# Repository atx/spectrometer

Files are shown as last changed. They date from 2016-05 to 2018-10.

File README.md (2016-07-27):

# Alpha Spectrometer

Alpha spectrometer developed during my internship at the [IEAP](http://www.utef.cvut.cz/ieap).



Pu-239 Am-241 Cm-244 spectrum (on bare die BPW34 in vacuum)



## Protocol

### General structure

```
|----------|---------
|   type   | content...
|----------|---------
```

If the device receives a packet with invalid type, it responds with an ERROR
packet with EUNKNOWN error type.

### Host->Device

#### NOP

This does not do anything, it is recommended to send a bunch of NOPs on opening
the serial port to flush any data which might have been left in the device input
buffer.
```
|----------|
|   0x01   |
|----------|
```
#### PING

Used by host to check whether the device is alive. Device should respond with PONG.
```
|----------|
|   0x02   |
|----------|
```
#### GET

Used by host to get basic properties. Device should respond with GETRESP.
```
|----------|---------|
|   0x03   | propid  |
|----------|---------|
```
#### SET

Used by host to set basic properties. Propval length depends on the property being
set. Note that multi byte values should be sent in little endian.
```
|----------|---------|----------
|   0x04   | propid  | propval...
|----------|---------|----------
```
#### START

Start sampling and sending events.
```
|----------|
|   0x05   |
|----------|
```
#### END

End sampling and sending events.
```
|----------|
|   0x06   |
|----------|
```
### Device->Host

The most significant bit of the type field is always set to 1.

#### PONG

Sent as response to host PING.
```
|----------|
|   0x82   |
|----------|
```
#### EVENT

Send event (little endian).
```
|----------|----------|----------|
|   0x87   |   low    |   high   |
|----------|----------|----------|
```
#### GETRESP
```
|----------|----------|----------
|   0x83   |  propid  |  value...
|----------|----------|----------
```
The value length depends on the propid and the byte order is little endian.

#### WAVE

Sends event waveform. This is currently not yet implemented.
```
|----------|----------|----------
|   0x88   |  length  |  <length> samples, 2 bytes each, Big endian
|----------|----------|----------
```
#### ERROR
```
|----------|----------|
|   0xff   |  errno   |
|----------|----------|
```
Sent on errors.
errno:
  =  1  EUNKNOWN
    -- Sent on unknown packet type received
  =  2  EINKEY
    -- Sent on invalid key in GET/SET packet
  =  3  EINOP
    -- Sent on invalid operation on an existing key (unsuported read/write)

### Properties

#### PROP_FW (0x01)
length = 2

Firmware version version.

#### PROP_THRESH (0x02)
length = 2

Event trigger threshold.

#### PROP_BIAS (0x03)
length = 1

Set to 1 if the internal bias generator should be enabled.

#### PROP_AMP (0x04)
length = 1

Set to 1 if the internal x6 amplifier should be enabled.

#### PROP_RTHRESH (0x05)
length = 2

If the value is > 0, the events are further filtered based on whether their falling edge
is at least N samples longer than the rising edge.

#### PROP_SERNO (0x06)
length = 2

Serial number of the device. Set at compile time using `make SERNO=X`

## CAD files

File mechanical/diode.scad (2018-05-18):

difference() {
	minkowski() {
		cube([16, 16, 6], center=true);
		cylinder(r=2, h=0.01, $fn=100);
	}
	translate([0, 0, -0.5])
		cube([17, 15.5, 4], center=true);
	translate([0, 0, 2])
		cube([9, 3, 5], center=true);
}

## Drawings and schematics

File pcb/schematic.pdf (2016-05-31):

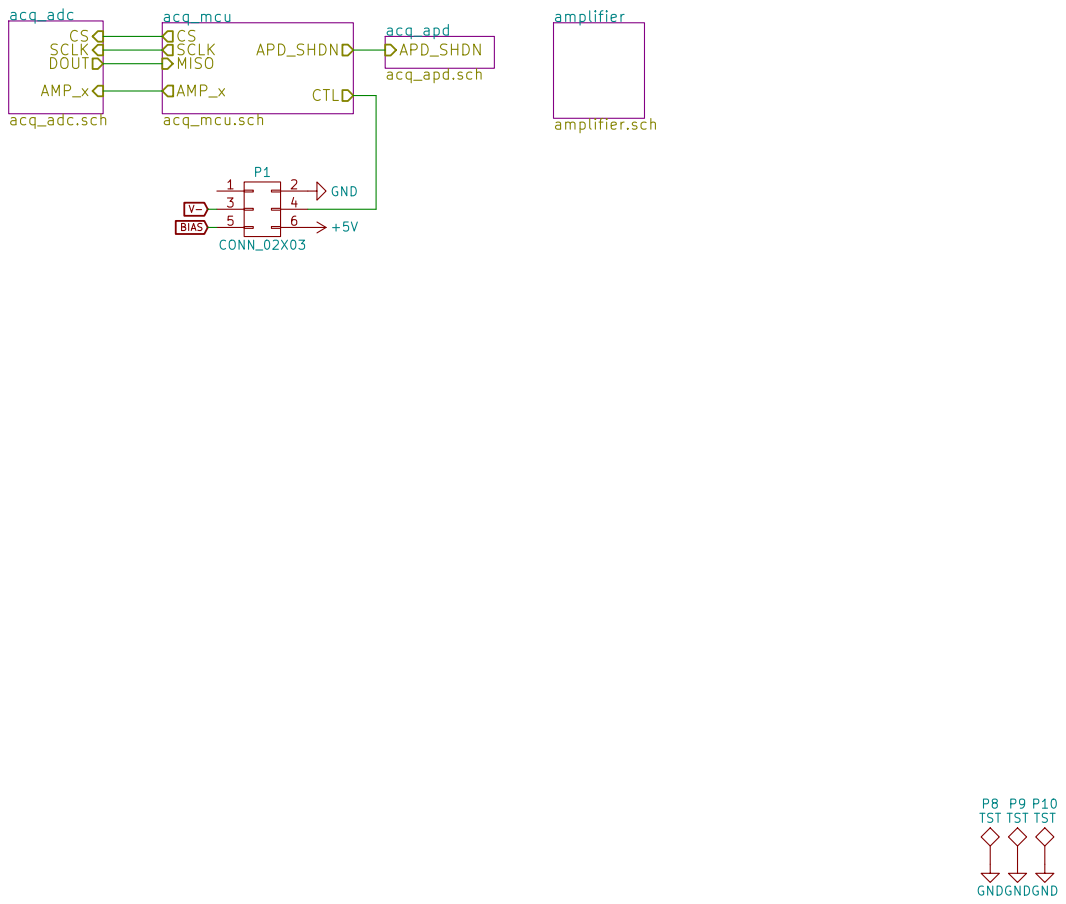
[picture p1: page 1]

Institute of Experimental and Applied Physics P8 TST GND

File: pcb.sch Sheet: /
Id: 1/5 Title: Root

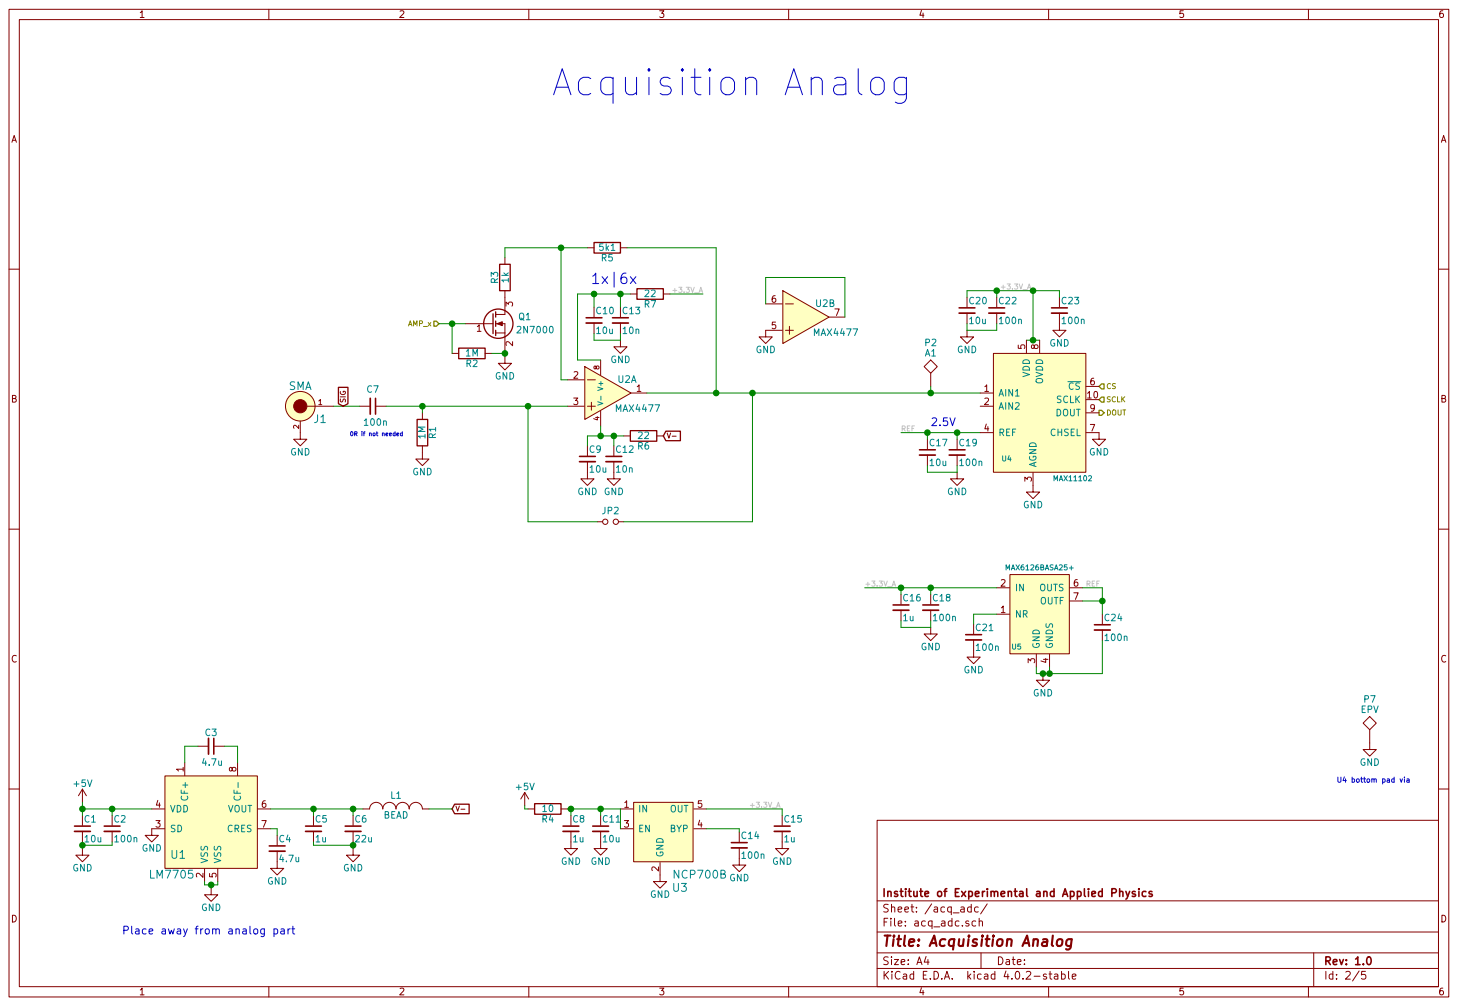
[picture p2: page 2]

U4 bottom pad via SIG

Institute of Experimental and Applied Physics
Sheet: /acq_adc/
File: acq_adc.sch
Id: 2/5 Title: Acquisition Analog

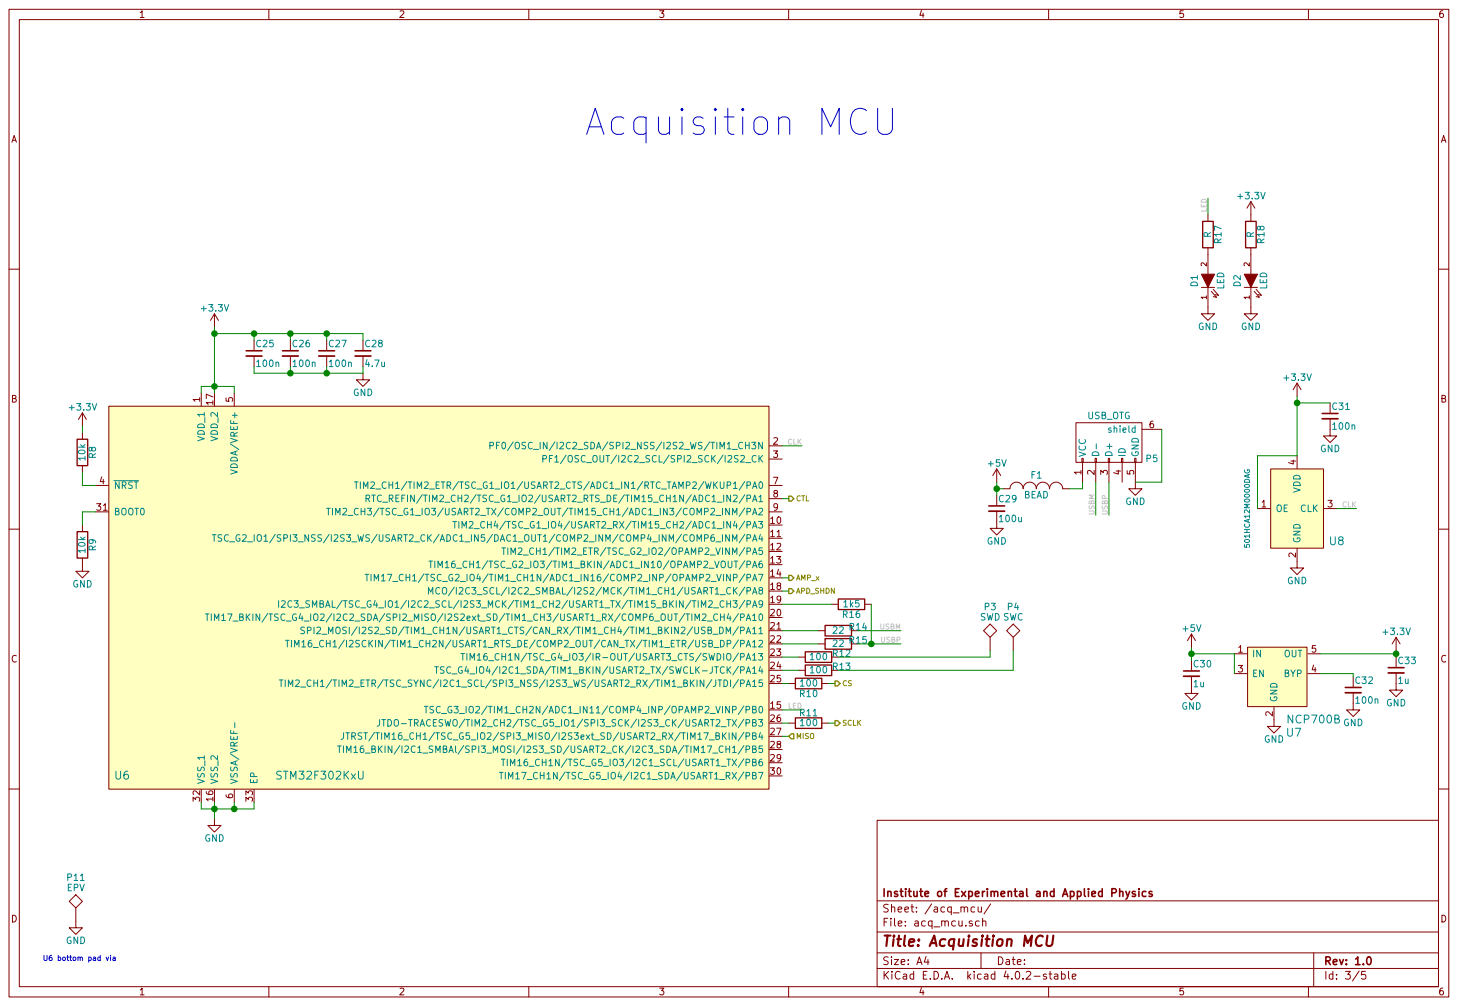
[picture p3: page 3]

5 VSSA/VREF- 6 TIM2_CH1/TIM2_ETR/TSC_G1_IO1/USART2_CTS/ADC1_IN1/RTC_TAMP2/WKUP1/PA0 7 RTC_REFIN/TIM2_CH2/TSC_G1_IO2/USART2_RTS_DE/TIM15_CH1N/ADC1_IN2/PA1 8 TIM2_CH3/TSC_G1_IO3/USART2_TX/COMP2_OUT/TIM15_CH1/ADC1_IN3/COMP2_INM/PA2 9 TIM2_CH4/TSC_G1_IO4/USART2_RX/TIM15_CH2/ADC1_IN4/PA3 10 TIM17_BKIN/TSC_G4_IO2/I2C2_SDA/SPI2_MISO/I2S2ext_SD/TIM1_CH3/USART1_RX/COMP6_OUT/TIM2_CH4/PA10 20 TIM17_CH1N/TSC_G5_IO4/I2C1_SDA/USART1_RX/PB7 30 TSC_G2_IO1/SPI3_NSS/I2S3_WS/USART2_CK/ADC1_IN5/DAC1_OUT1/COMP2_INM/COMP4_INM/COMP6_INM/PA4 11 SPI2_MOSI/I2S2_SD/TIM1_CH1N/USART1_CTS/CAN_RX/TIM1_CH4/TIM1_BKIN2/USB_DM/PA11 21 BOOT0 31 TIM2_CH1/TIM2_ETR/TSC_G2_IO2/OPAMP2_VINM/PA5 12 TIM16_CH1/I2SCKIN/TIM1_CH2N/USART1_RTS_DE/COMP2_OUT/CAN_TX/TIM1_ETR/USB_DP/PA12 22 VSS_1 32 TIM16_CH1/TSC_G2_IO3/TIM1_BKIN/ADC1_IN10/OPAMP2_VOUT/PA6 13 TIM16_CH1N/TSC_G4_IO3/IR-OUT/USART3_CTS/SWDIO/PA13 23 EP 33 TIM17_CH1/TSC_G2_IO4/TIM1_CH1N/ADC1_IN16/COMP2_INP/OPAMP2_VINP/PA7 14 TSC_G4_IO4/I2C1_SDA/TIM1_BKIN/USART2_TX/SWCLK-JTCK/PA14 24 TSC_G3_IO2/TIM1_CH2N/ADC1_IN11/COMP4_INP/OPAMP2_VINP/PB0 15 TIM2_CH1/TIM2_ETR/TSC_SYNC/I2C1_SCL/SPI3_NSS/I2S3_WS/USART2_RX/TIM1_BKIN/JTDI/PA15 25 VSS_2 16

Institute of Experimental and Applied Physics
Sheet: /acq_mcu/
File: acq_mcu.sch
Id: 3/5 Title: Acquisition MCU

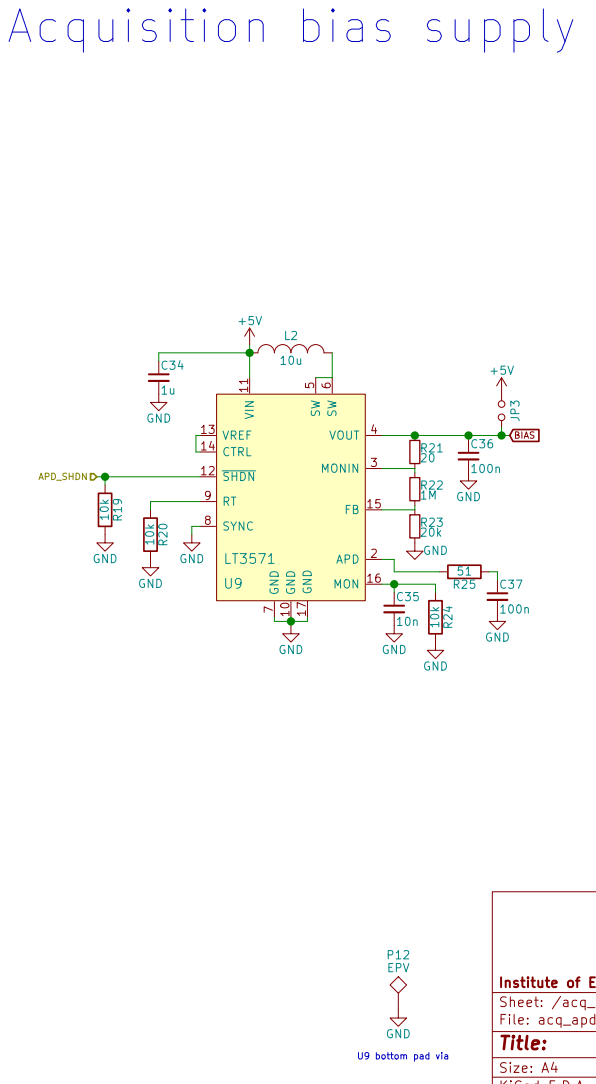
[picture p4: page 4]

7 SYNC 8 RT 9 GND 10 VIN 11 SHDN 12 VREF 13 CTRL 14 FB 15 MON 16 GND 17 U9

LT3571 GND GND 10k R20 GND 10k R19 GND

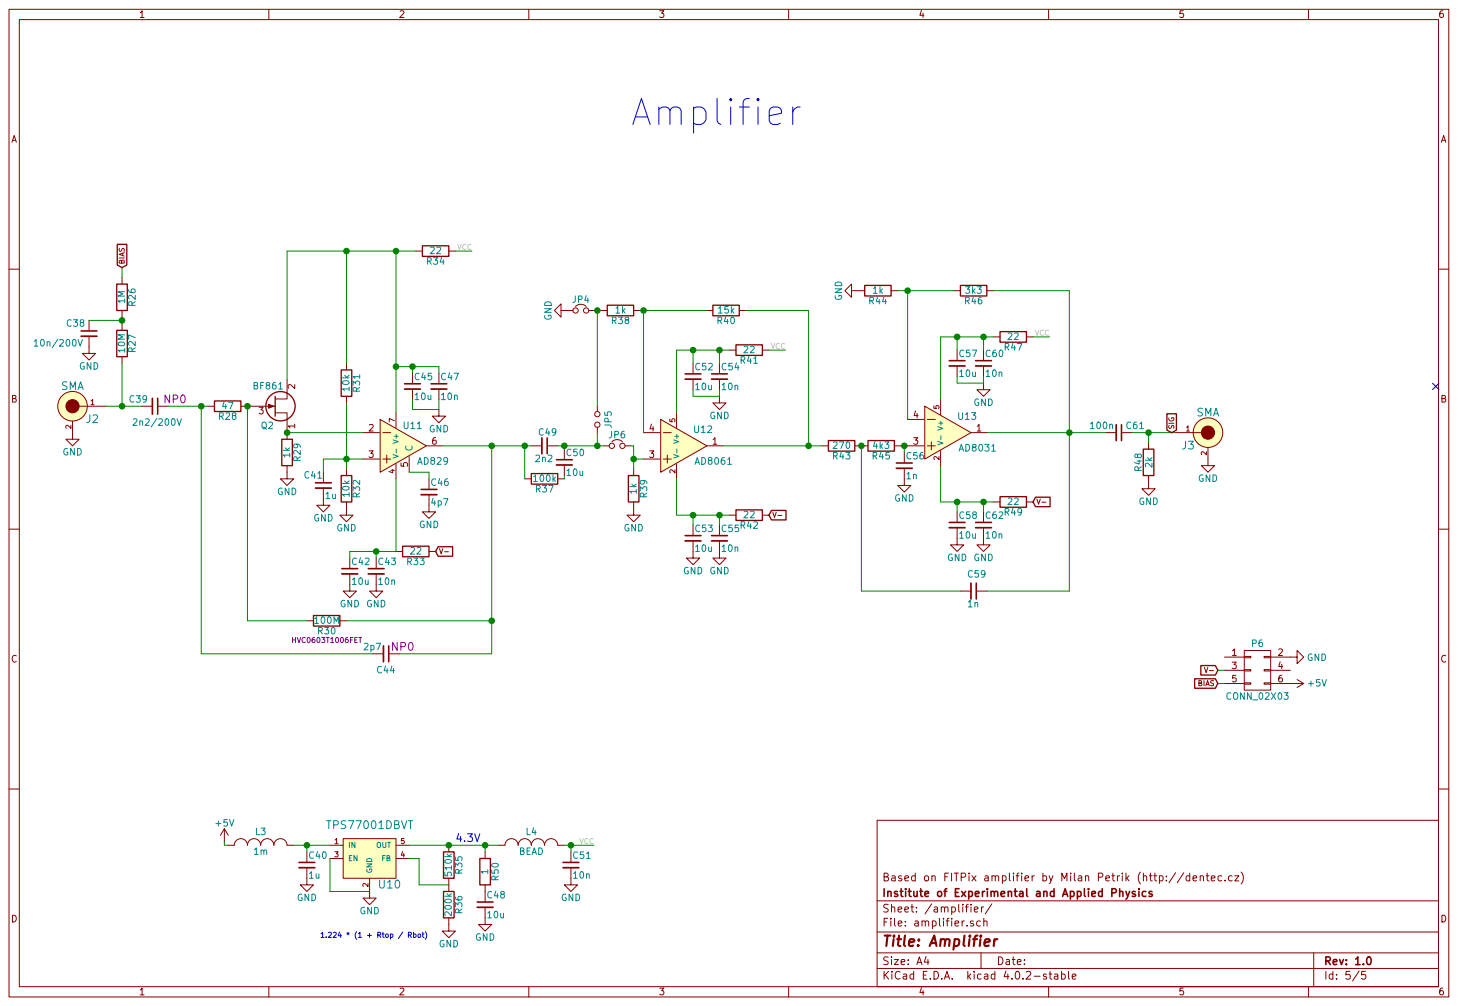
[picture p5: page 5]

2 EN 3 FB 4 OUT 5 U10 TPS77001DBVT GND

Based on FITPix amplifier by Milan Petrik (http://dentec.cz)
Institute of Experimental and Applied Physics
Sheet: /amplifier/
File: amplifier.sch
Id: 5/5 Title: Amplifier

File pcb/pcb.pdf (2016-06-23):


Institute of Experimental and Applied Physics P8 TST GND

File: pcb.sch Sheet: /
Id: 1/5 Title: Root

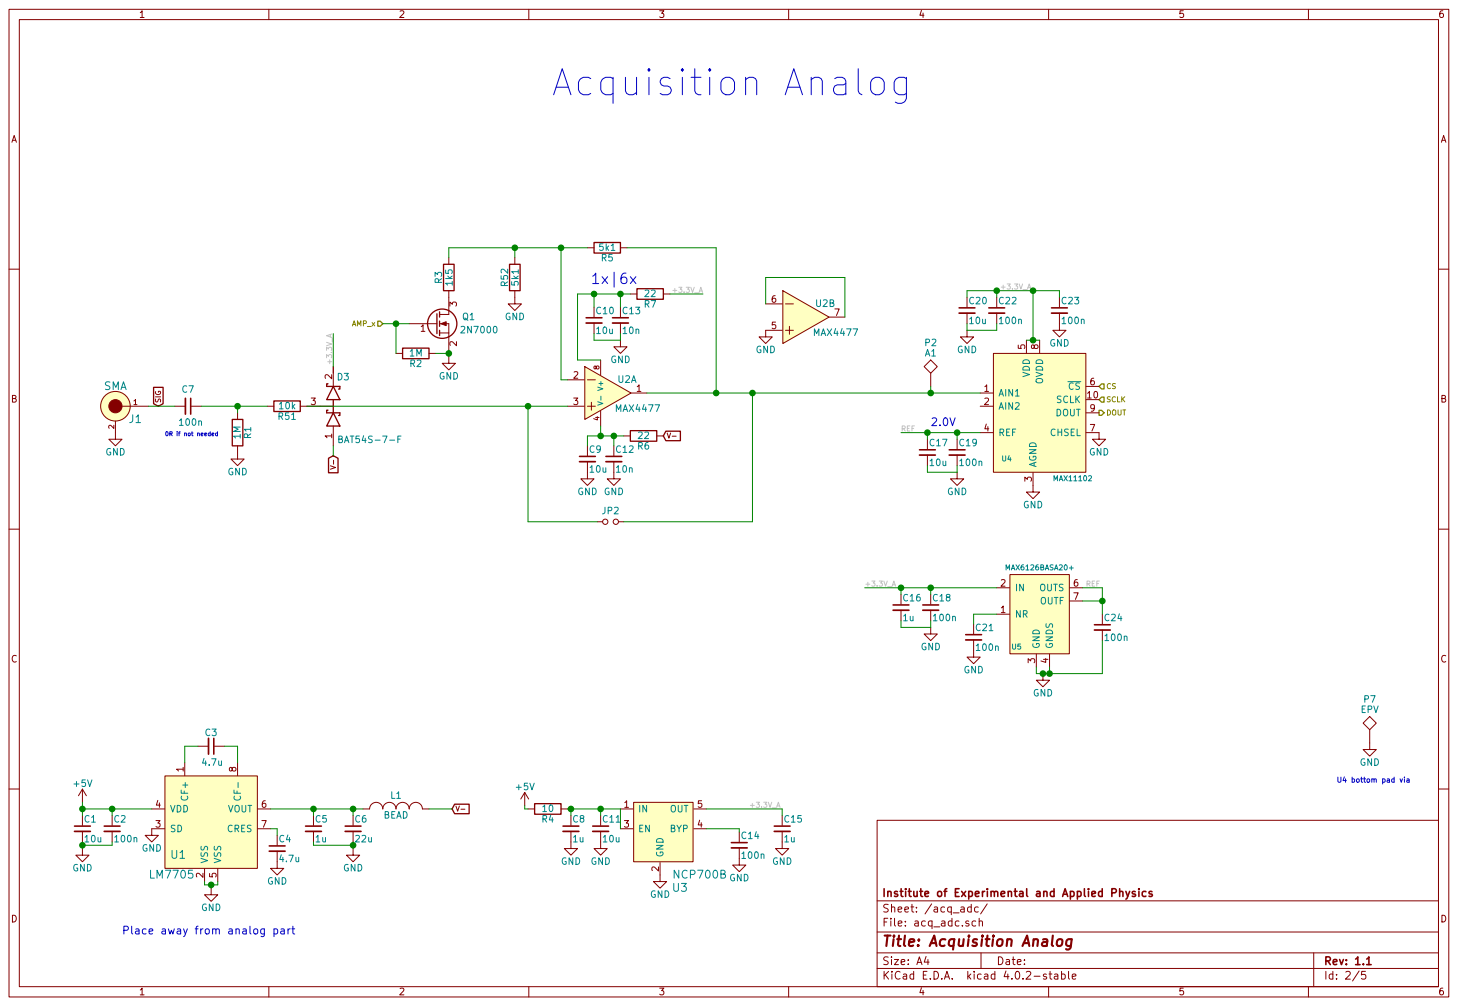
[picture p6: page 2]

U4 bottom pad via SIG

Institute of Experimental and Applied Physics
Sheet: /acq_adc/
File: acq_adc.sch
Id: 2/5 Title: Acquisition Analog

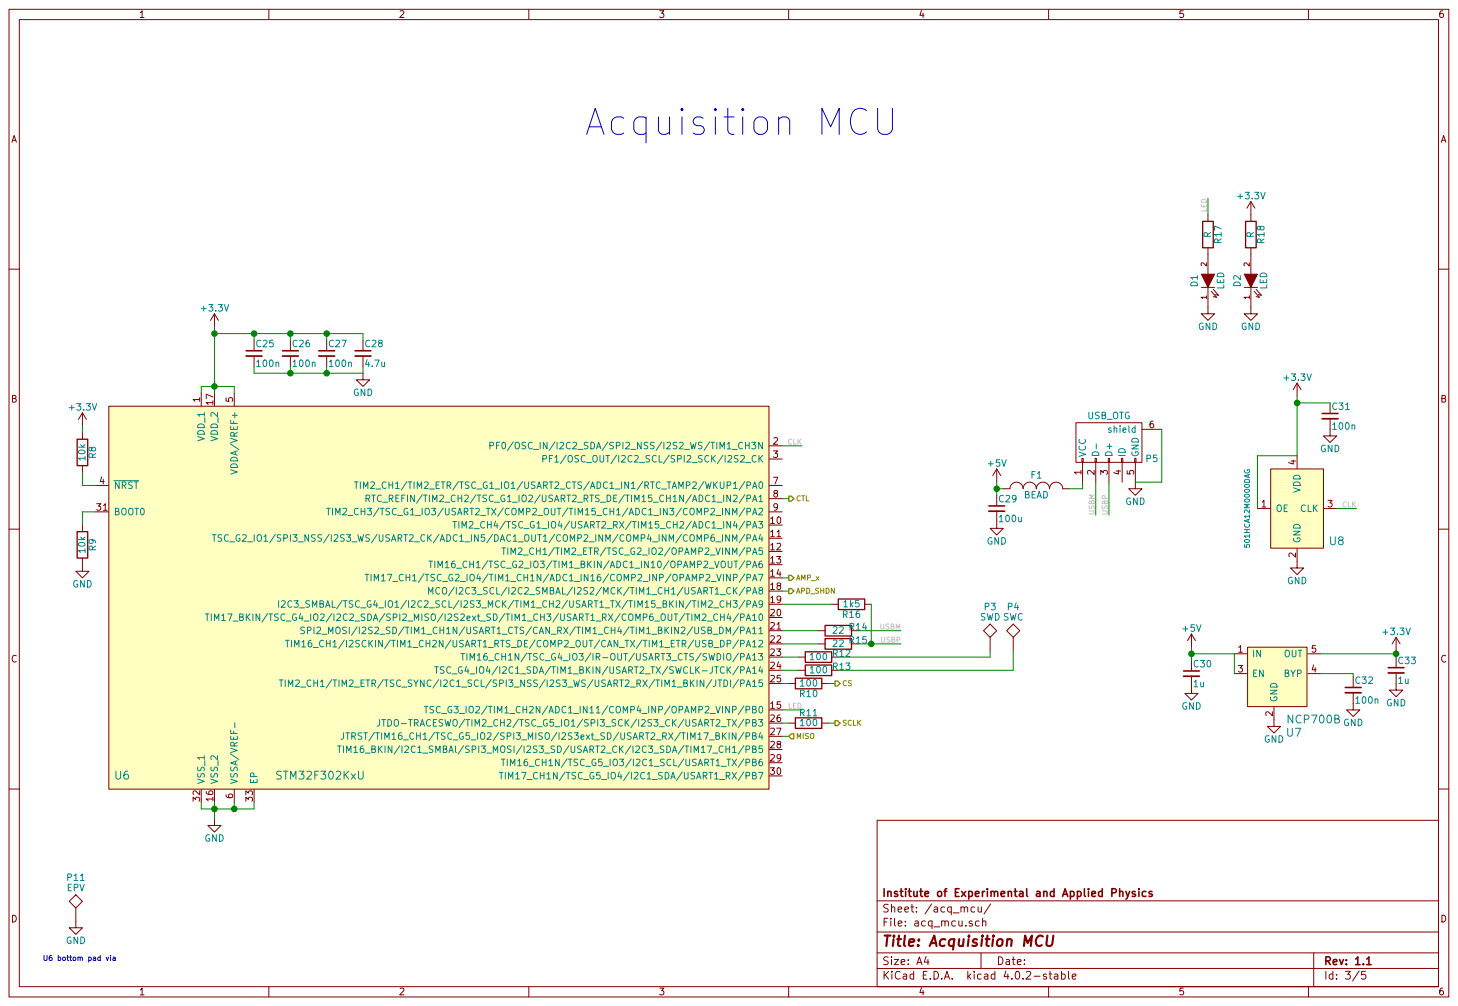
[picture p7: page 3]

5 VSSA/VREF- 6 TIM2_CH1/TIM2_ETR/TSC_G1_IO1/USART2_CTS/ADC1_IN1/RTC_TAMP2/WKUP1/PA0 7 RTC_REFIN/TIM2_CH2/TSC_G1_IO2/USART2_RTS_DE/TIM15_CH1N/ADC1_IN2/PA1 8 TIM2_CH3/TSC_G1_IO3/USART2_TX/COMP2_OUT/TIM15_CH1/ADC1_IN3/COMP2_INM/PA2 9 TIM2_CH4/TSC_G1_IO4/USART2_RX/TIM15_CH2/ADC1_IN4/PA3 10 TIM17_BKIN/TSC_G4_IO2/I2C2_SDA/SPI2_MISO/I2S2ext_SD/TIM1_CH3/USART1_RX/COMP6_OUT/TIM2_CH4/PA10 20 TIM17_CH1N/TSC_G5_IO4/I2C1_SDA/USART1_RX/PB7 30 TSC_G2_IO1/SPI3_NSS/I2S3_WS/USART2_CK/ADC1_IN5/DAC1_OUT1/COMP2_INM/COMP4_INM/COMP6_INM/PA4 11 SPI2_MOSI/I2S2_SD/TIM1_CH1N/USART1_CTS/CAN_RX/TIM1_CH4/TIM1_BKIN2/USB_DM/PA11 21 BOOT0 31 TIM2_CH1/TIM2_ETR/TSC_G2_IO2/OPAMP2_VINM/PA5 12 TIM16_CH1/I2SCKIN/TIM1_CH2N/USART1_RTS_DE/COMP2_OUT/CAN_TX/TIM1_ETR/USB_DP/PA12 22 VSS_1 32 TIM16_CH1/TSC_G2_IO3/TIM1_BKIN/ADC1_IN10/OPAMP2_VOUT/PA6 13 TIM16_CH1N/TSC_G4_IO3/IR-OUT/USART3_CTS/SWDIO/PA13 23 EP 33 TIM17_CH1/TSC_G2_IO4/TIM1_CH1N/ADC1_IN16/COMP2_INP/OPAMP2_VINP/PA7 14 TSC_G4_IO4/I2C1_SDA/TIM1_BKIN/USART2_TX/SWCLK-JTCK/PA14 24 TSC_G3_IO2/TIM1_CH2N/ADC1_IN11/COMP4_INP/OPAMP2_VINP/PB0 15 TIM2_CH1/TIM2_ETR/TSC_SYNC/I2C1_SCL/SPI3_NSS/I2S3_WS/USART2_RX/TIM1_BKIN/JTDI/PA15 25 VSS_2 16

Institute of Experimental and Applied Physics
Sheet: /acq_mcu/
File: acq_mcu.sch
Id: 3/5 Title: Acquisition MCU


7 SYNC 8 RT 9 GND 10 VIN 11 SHDN 12 VREF 13 CTRL 14 FB 15 MON 16 GND 17 U9

LT3571 GND GND 10k R20 GND 10k R19 GND

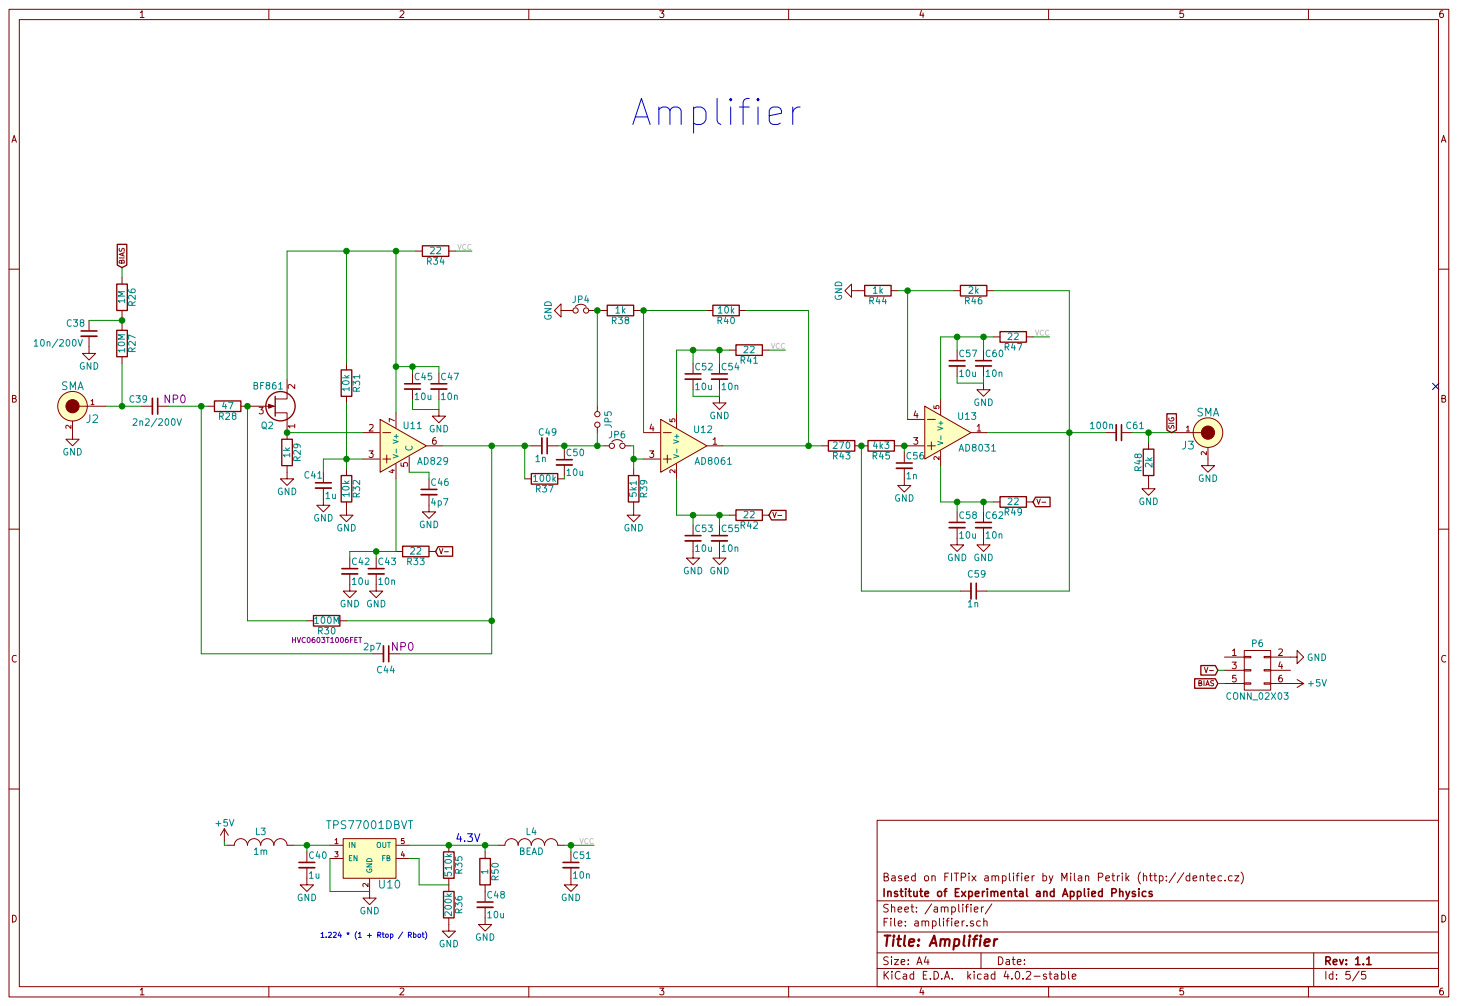
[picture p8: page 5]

2 EN 3 FB 4 OUT 5 U10 TPS77001DBVT GND

Based on FITPix amplifier by Milan Petrik (http://dentec.cz)
Institute of Experimental and Applied Physics
Sheet: /amplifier/
File: amplifier.sch
Id: 5/5 Title: Amplifier

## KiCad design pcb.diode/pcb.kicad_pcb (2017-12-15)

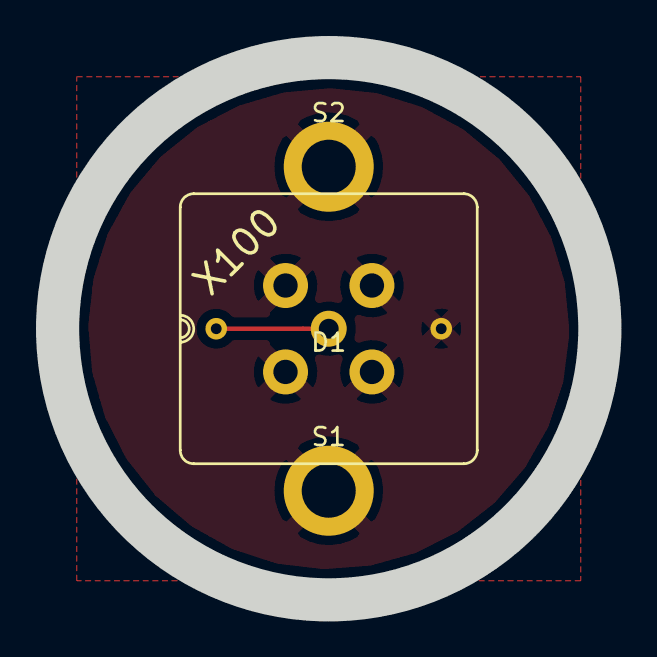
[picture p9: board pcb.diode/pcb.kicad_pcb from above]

Board: 2 copper layers, 30.1 x 30.1 mm, 4 parts (1 on the bottom side), 2 nets.

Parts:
D1: X100; X100-7-THD
J1: SMA; SMA_STRAIGHT_PCB_LPRS
S1, S2: M2; Measurement_Point_Round-TH_Big

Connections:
unnamed: D1.1, J1.1
unnamed: D1.2, J1.2, J1.3, J1.4, J1.5, S1.1, S2.1

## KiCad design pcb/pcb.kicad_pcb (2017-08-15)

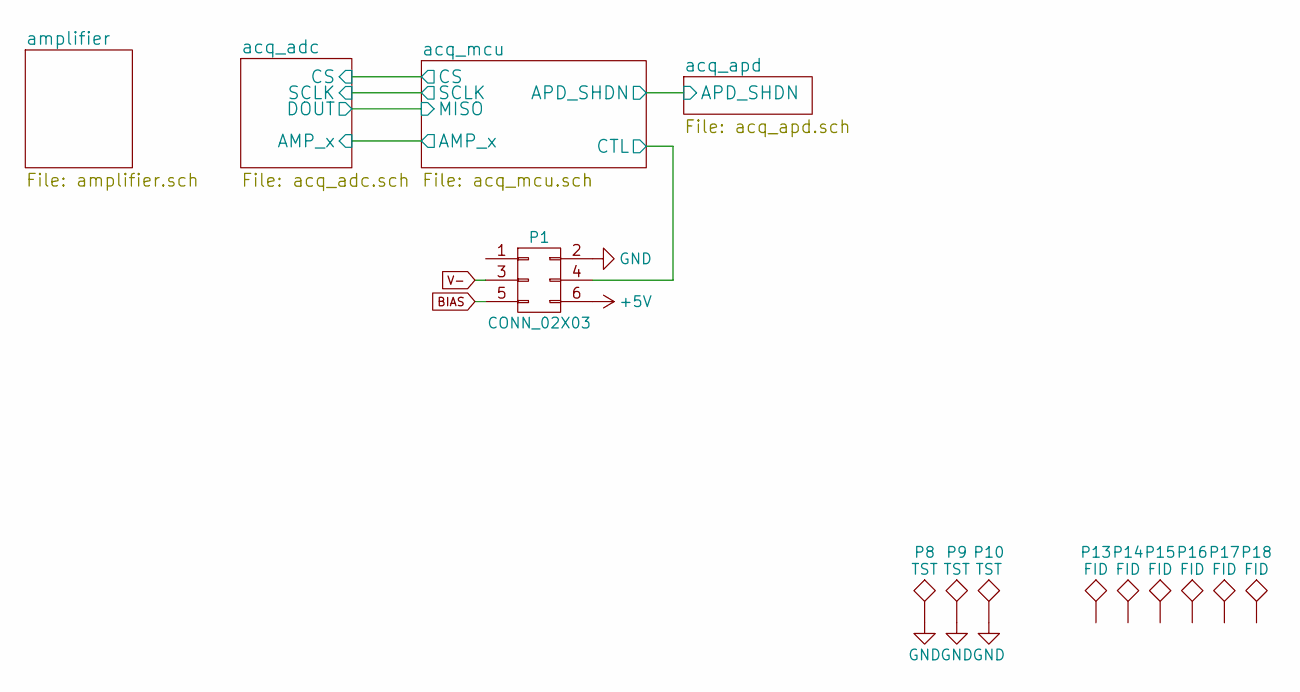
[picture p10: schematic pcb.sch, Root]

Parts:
P1: CONN_02X03; CONN_02x03_EDGE
P8, P9, P10: TST; Measurement_Point_Round-TH_Big
P13, P14, P15, P16, P17, P18: FID; Fiducial_1mm_Dia_2.54mm_Outer_CopperTop

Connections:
+5V: P1.6; also elsewhere on the board
/acq_mcu/CTL: P1.4; also elsewhere on the board
BIAS: P1.5; also elsewhere on the board
GND: P1.2, P8.1, P9.1, P10.1; also elsewhere on the board
V-: P1.3; also elsewhere on the board

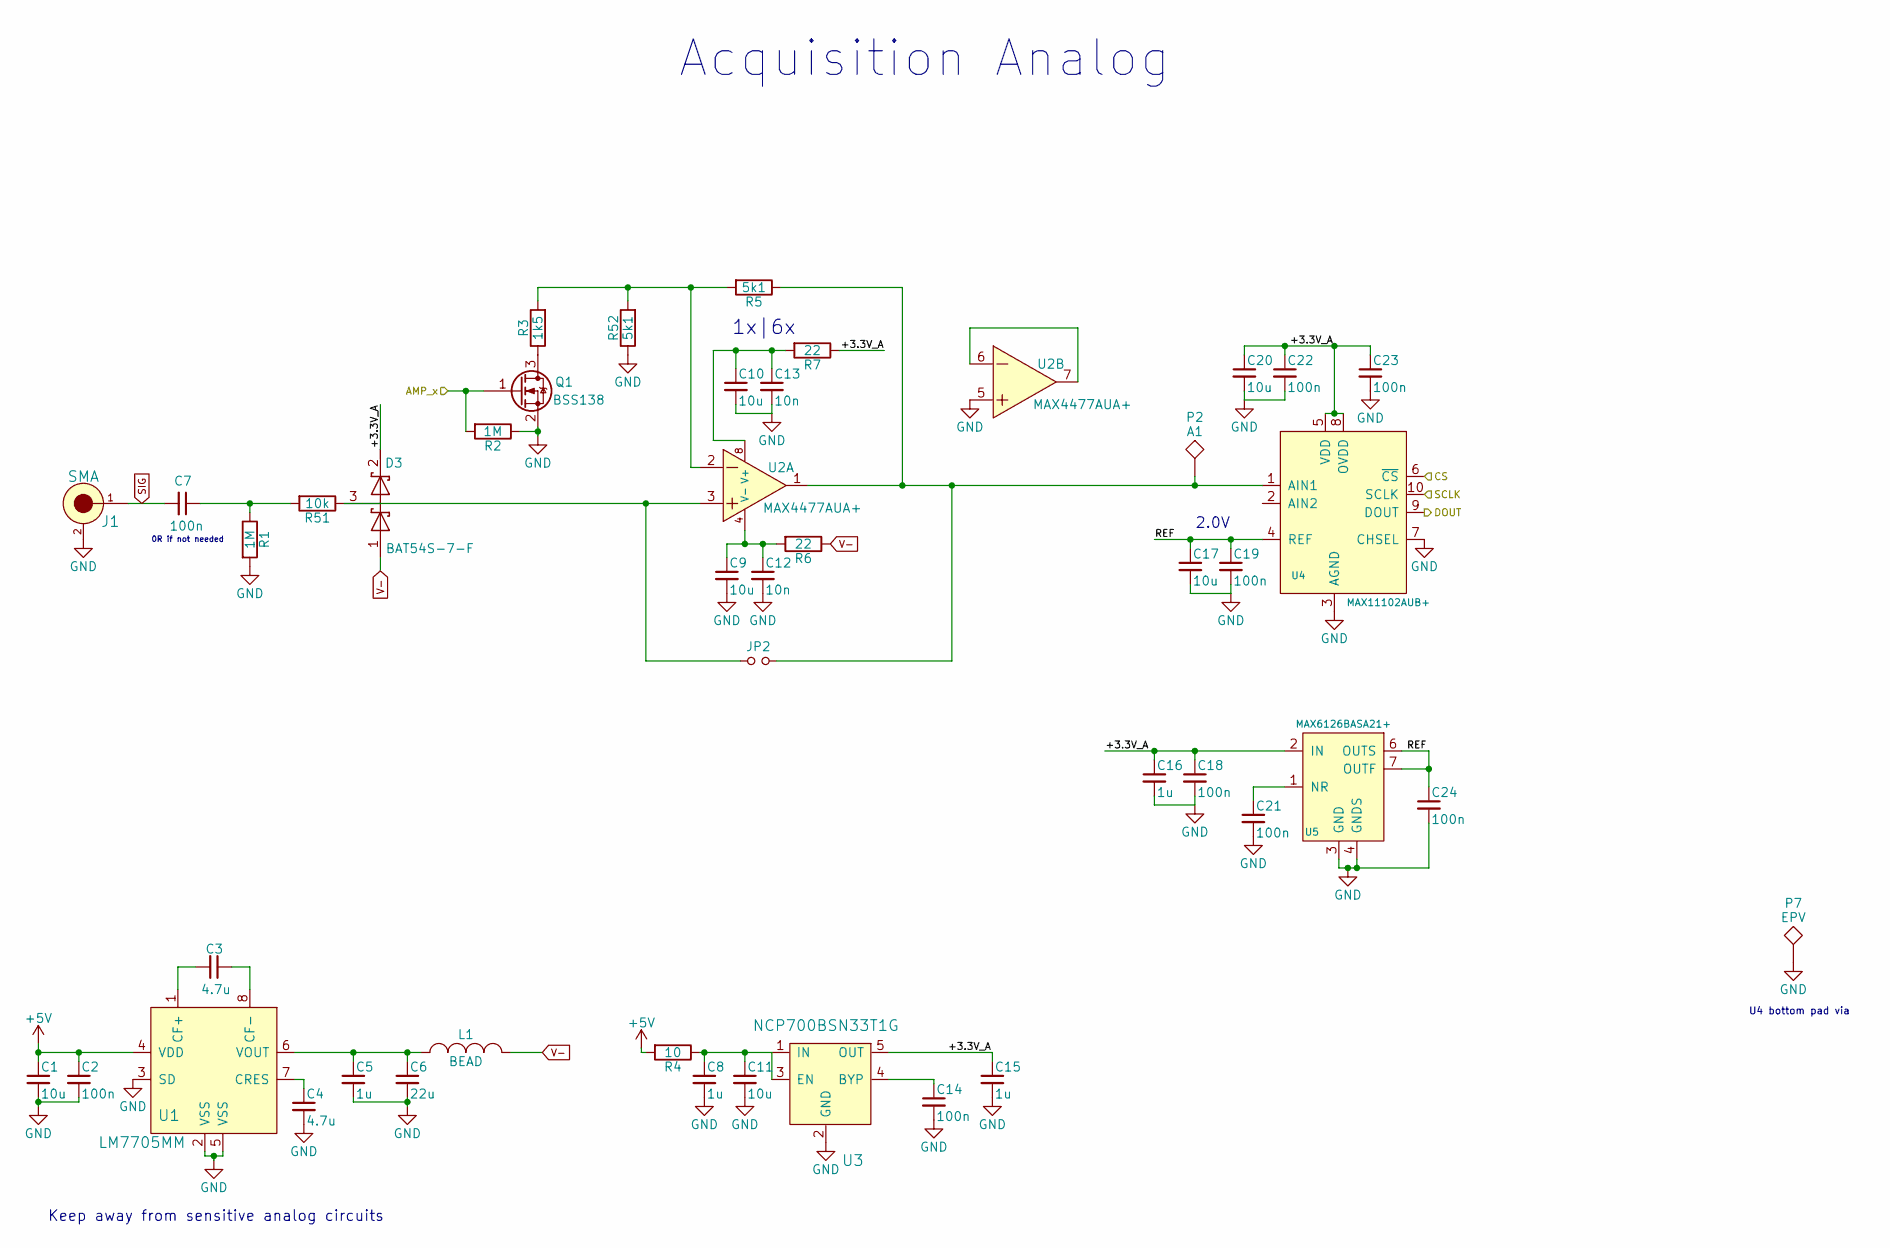
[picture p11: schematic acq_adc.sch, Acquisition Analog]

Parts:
C1, C9, C10, C11, C17, C20: 10u; R_0805
C2, C7, C14, C18, C19, C21, C22, C23, C24: 100n; R_0402
C3, C4: 4.7u; R_0603
C5, C8, C15, C16: 1u; R_0402
C6: 22u; R_0805
C12, C13: 10n; R_0402
D3: BAT54S-7-F; SOT-23
J1: SMA; CON-SMA-EDGE
JP2: DNP; R_0402
L1: BEAD; R_0402
P2: A1; Measurement_Point_Round-SMD-Pad_Big
P7: EPV; Measurement_Point_Round-TH_Small
Q1: BSS138; SOT-23
R1, R2: 1M; R_0402
R3: 1k5; R_0402
R4: 10; R_0402
R5, R52: 5k1; R_0402
R6, R7: 22; R_0402
R51: 10k; R_0402
U1: LM7705MM; MSOP-8_3x3mm_Pitch0.65mm
U2: MAX4477AUA+; MSOP-8_3x3mm_Pitch0.65mm
U3: NCP700BSN33T1G; SOT-23-5
U4: MAX11102AUB+; uMAX-10-EP
U5: MAX6126BASA21+; SOIC-8_3.9x4.9mm_Pitch1.27mm

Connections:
+5V: C1.1, C2.1, R4.2, U1.4 (VDD); also elsewhere on the board
/acq_adc/+3.3V_A: C15.1, C16.1, C18.1, C20.1, C22.1, C23.1, D3.2 (K), R7.1, U3.5 (OUT), U4.5 (VDD), U4.8 (OVDD), U5.2 (IN)
/acq_adc/AMP_x: Q1.1 (G), R2.2; also elsewhere on the board
/acq_adc/CS: U4.6 (~CS); also elsewhere on the board
/acq_adc/DOUT: U4.9 (DOUT); also elsewhere on the board
/acq_adc/REF: C17.1, C19.1, C24.1, U4.4 (REF), U5.6 (OUTS), U5.7 (OUTF)
/acq_adc/SCLK: U4.10 (SCLK); also elsewhere on the board
GND: C1.2, C2.2, C4.2, C5.2, C6.2, C8.2, C9.2, C10.2, C11.2, C12.2, C13.2, C14.2, C15.2, C16.2, C17.2, C18.2, C19.2, C20.2, C21.2, C22.2, C23.2, C24.2, J1.2, J1.3, J1.4, J1.5, P7.1, Q1.2 (S), R1.2, R2.1, R52.1, U1.2 (VSS), U1.3 (SD), U1.5 (VSS), U2.5, U3.2 (GND), U4.3 (AGND), U4.7 (CHSEL), U4.11 (EP), U5.3 (GND), U5.4 (GNDS); also elsewhere on the board
unnamed: C3.1, U1.8 (CF-)
unnamed: C3.2, U1.1 (CF+)
unnamed: C4.1, U1.7 (CRES)
unnamed: C5.1, C6.1, L1.1, U1.6 (VOUT)
unnamed: C7.1, R1.1, R51.2
unnamed: C10.1, C13.1, R7.2, U2.8 (V+)
unnamed: C8.1, C11.1, R4.1, U3.1 (IN), U3.3 (EN)
unnamed: C9.1, C12.1, R6.2, U2.4 (V-)
unnamed: C14.1, U3.4 (BYP)
unnamed: C21.1, U5.1 (NR)
unnamed: D3.3 (common), JP2.1, R51.1, U2.3
unnamed: JP2.2, P2.1, R5.1, U2.1, U4.1 (AIN1)
unnamed: Q1.3 (D), R3.1
unnamed: R3.2, R5.2, R52.2, U2.2
unnamed: U2.6, U2.7
SIG: C7.2, J1.1; also elsewhere on the board
V-: D3.1 (A), L1.2, R6.1; also elsewhere on the board

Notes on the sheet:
Acquisition Analog
0R if not needed
1x|6x
2.0V
Keep away from sensitive analog circuits
U4 bottom pad via

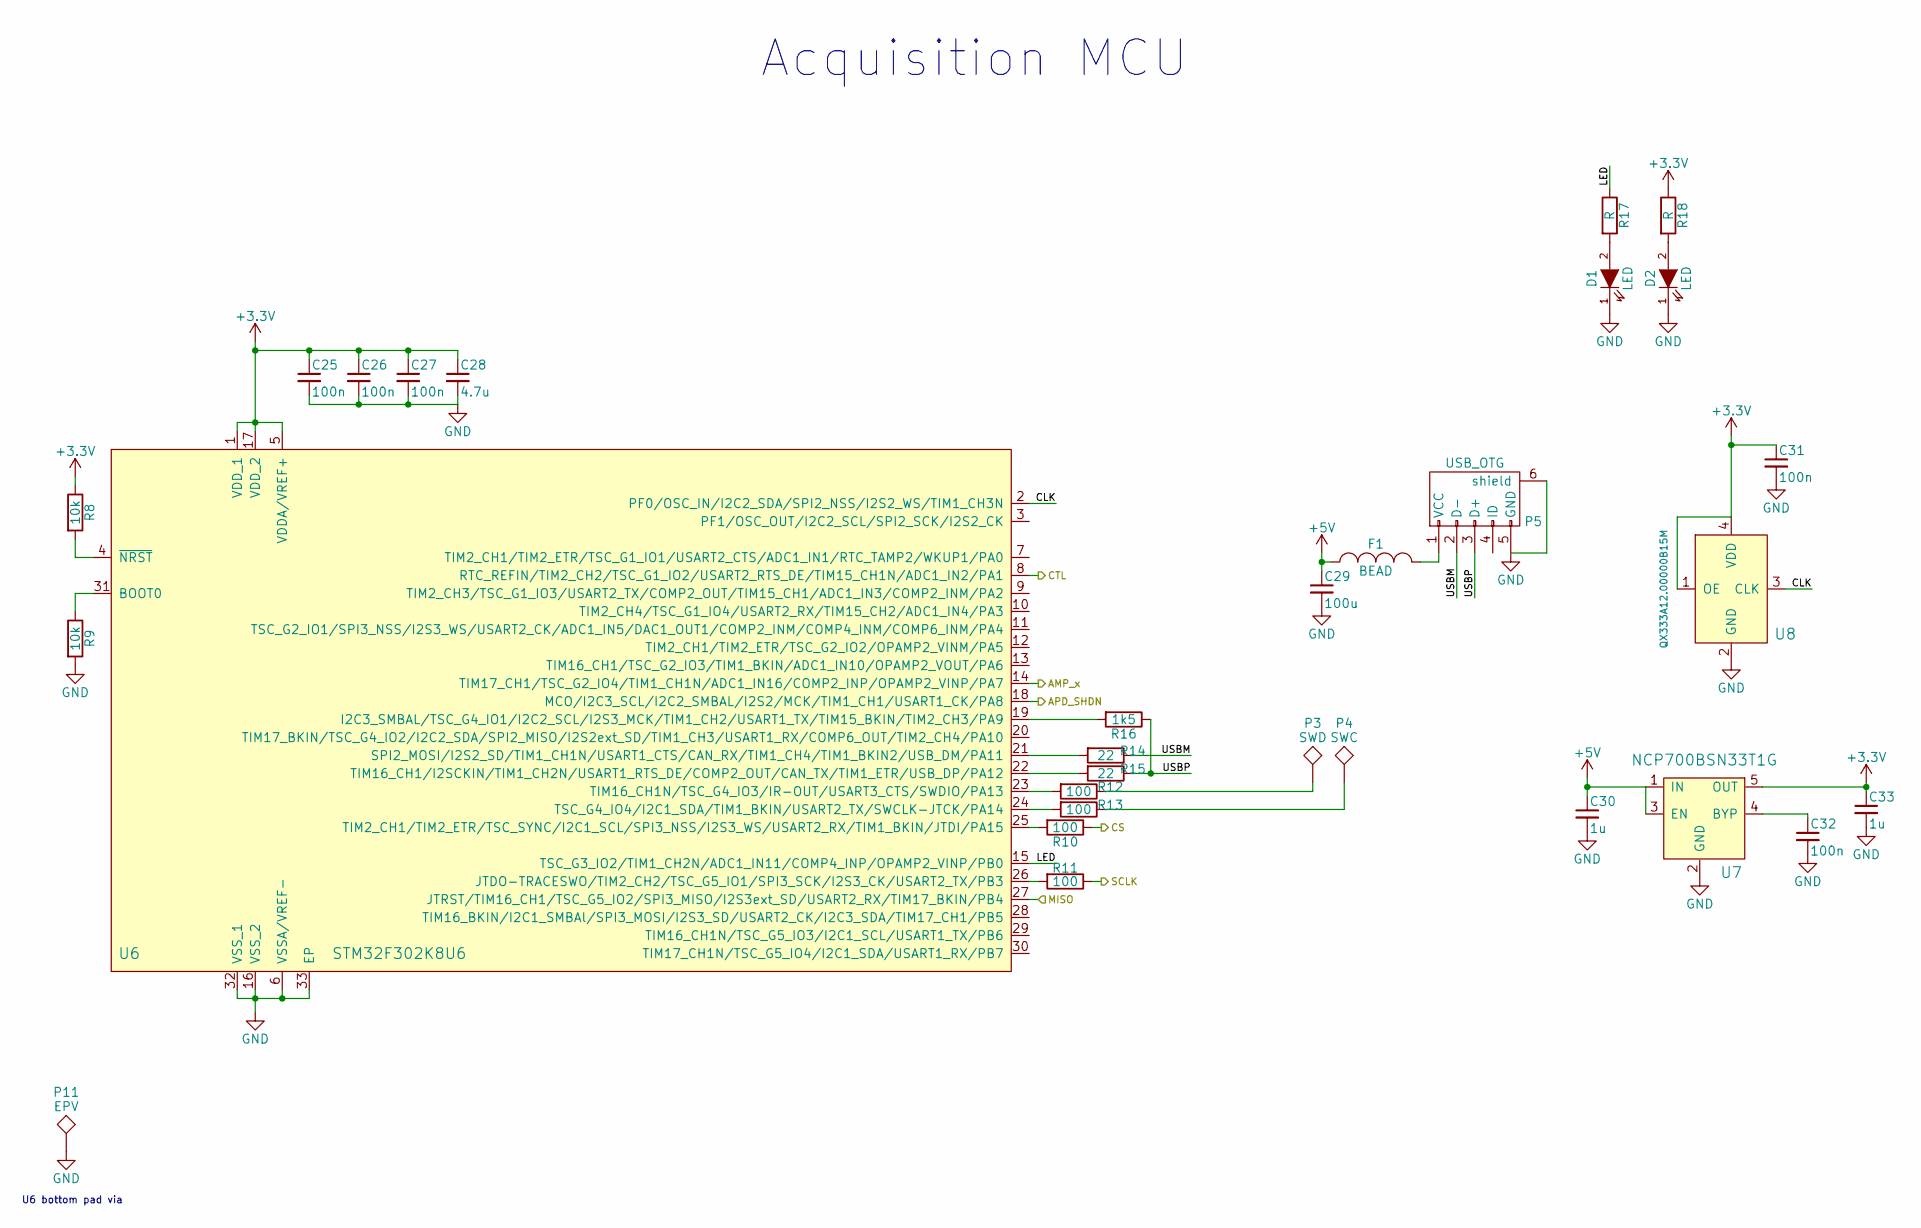
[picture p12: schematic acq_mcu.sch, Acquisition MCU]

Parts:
C25, C26, C27, C31, C32: 100n; R_0402
C28: 4.7u; R_0603
C29: 100u; TantalC_SizeB_EIA-3528_Reflow
C30, C33: 1u; R_0402
D1, D2: LED; R_0603
F1: BEAD; R_0402
P3: SWD; Measurement_Point_Round-SMD-Pad_Big
P4: SWC; Measurement_Point_Round-SMD-Pad_Big
P5: USB_OTG; USB_Micro-B
P11: EPV; Measurement_Point_Round-TH_Small
R8, R9: 10k; R_0402
R10, R11, R12, R13: 100; R_0402
R14, R15: 22; R_0402
R16: 1k5; R_0402
R17, R18: R; R_0402
U6: STM32F302K8U6; QFN-32-1EP_5x5mm_Pitch0.5mm
U7: NCP700BSN33T1G; SOT-23-5
U8: QX333A12.00000B15M; QX333A

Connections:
+3V3: C25.1, C26.1, C27.1, C28.1, C31.1, C33.1, R8.1, R18.1, U6.1 (VDD_1), U6.5 (VDDA/VREF+), U6.17 (VDD_2), U7.5 (OUT), U8.1 (OE), U8.4 (VDD)
+5V: C29.1, C30.1, F1.1, U7.1 (IN), U7.3 (EN); also elsewhere on the board
/acq_adc/AMP_x: U6.14 (TIM17_CH1/TSC_G2_IO4/TIM1_CH1N/ADC1_IN1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); also elsewhere on the board
/acq_adc/CS: R10.1; also elsewhere on the board
/acq_adc/DOUT: U6.27 (JTRST/TIM16_CH1/TSC_G5_IO2/SPI3_MISO/I2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); also elsewhere on the board
/acq_adc/SCLK: R11.1; also elsewhere on the board
/acq_apd/APD_SHDN: U6.18 (MCO/I2C3_SCL/I2C2_SMBAL/I2S2/MCK/TIM1_C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); also elsewhere on the board
/acq_mcu/CLK: U6.2 (PF0/OSC_IN/I2C2_SDA/SPI2_NSS/I2S2_WS/TI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), U8.3 (CLK)
/acq_mcu/CTL: U6.8 (RTC_REFIN/TIM2_CH2/TSC_G1_IO2/USART2_RT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); also elsewhere on the board
/acq_mcu/LED: R17.1, U6.15 (TSC_G3_IO2/TIM1_CH2N/ADC1_IN11/COMP4_IN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)
/acq_mcu/USBM: P5.2 (D-), R14.1
/acq_mcu/USBP: P5.3 (D+), R15.1, R16.1
GND: C25.2, C26.2, C27.2, C28.2, C29.2, C30.2, C31.2, C32.2, C33.2, D1.1 (K), D2.1 (K), P5.5 (GND), P5.6 (shield), P11.1, R9.2, U6.6 (VSSA/VREF-), U6.16 (VSS_2), U6.32 (VSS_1), U6.33 (EP), U7.2 (GND), U8.2 (GND); also elsewhere on the board
unnamed: C32.1, U7.4 (BYP)
unnamed: D1.2 (A), R17.2
unnamed: D2.2 (A), R18.2
unnamed: F1.2, P5.1 (VCC)
unnamed: P3.1, R12.1
unnamed: P4.1, R13.1
unnamed: R8.2, U6.4 (~NRST)
unnamed: R9.1, U6.31 (BOOT0)
unnamed: R10.2, U6.25 (TIM2_CH1/TIM2_ETR/TSC_SYNC/I2C1_SCL/SPI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)
unnamed: R11.2, U6.26 (JTDO-TRACESWO/TIM2_CH2/TSC_G5_IO1/SPI3_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)
unnamed: R12.2, U6.23 (TIM16_CH1N/TSC_G4_IO3/IR-OUT/USART3_CTS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)
unnamed: R13.2, U6.24 (TSC_G4_IO4/I2C1_SDA/TIM1_BKIN/USART2_TX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)
unnamed: R14.2, U6.21 (SPI2_MOSI/I2S2_SD/TIM1_CH1N/USART1_CTS/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)
unnamed: R15.2, U6.22 (TIM16_CH1/I2SCKIN/TIM1_CH2N/USART1_RTS_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)
unnamed: R16.2, U6.19 (I2C3_SMBAL/TSC_G4_IO1/I2C2_SCL/I2S3_MCK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)

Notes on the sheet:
Acquisition MCU
U6 bottom pad via

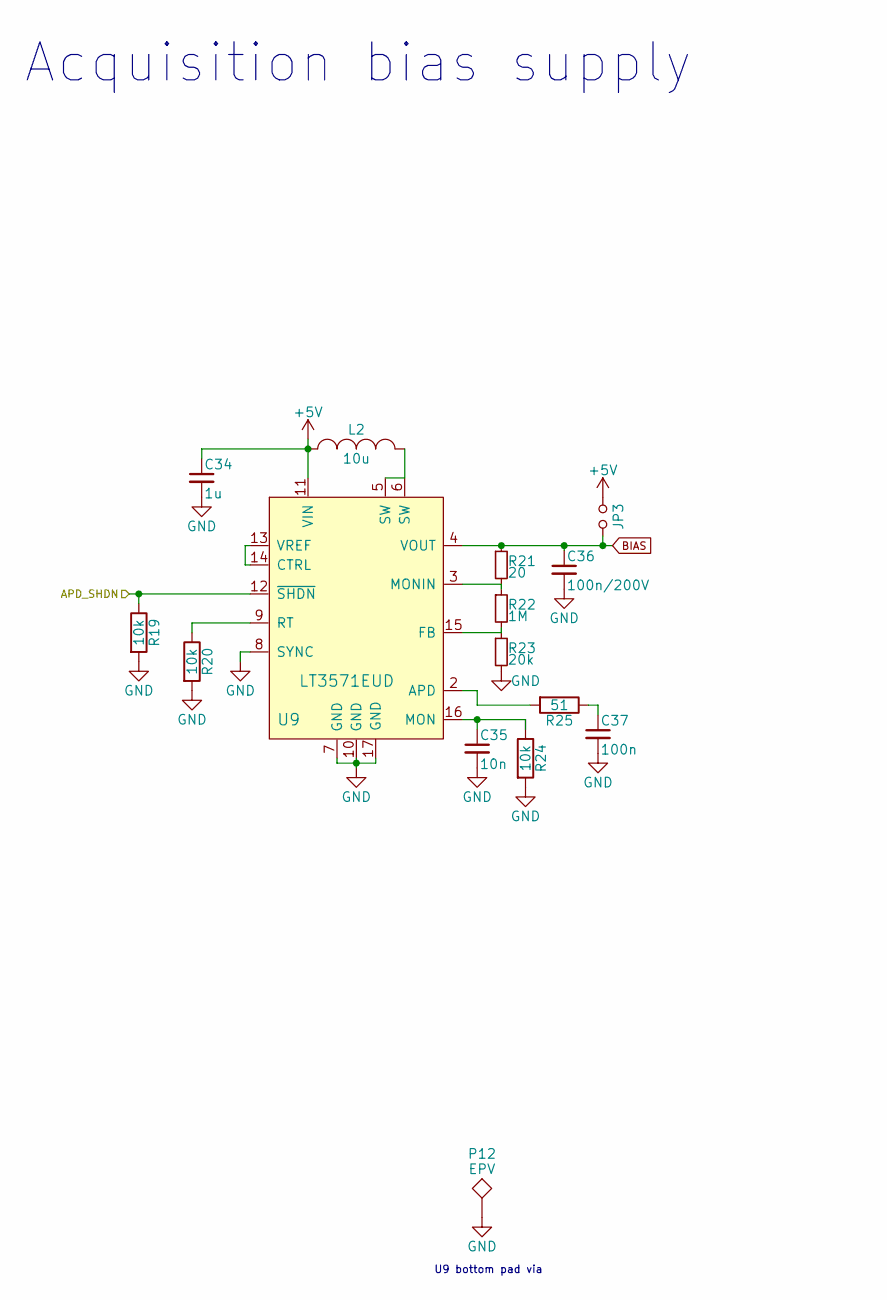
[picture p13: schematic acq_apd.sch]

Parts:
C34: 1u; R_0402
C35: 10n; R_0402
C36: 100n/200V; R_0805
C37: 100n; R_0402
JP3: DNP; R_0402
L2: 10u; R_1210
P12: EPV; Measurement_Point_Round-TH_Small
R19, R20, R24: 10k; R_0402
R21: 20; R_0402
R22: 1M; R_0402
R23: 20k; R_0402
R25: 51; R_0402
U9: LT3571EUD; QFN-16-1EP_3x3mm_Pitch0.5mm

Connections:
+5V: C34.1, JP3.1, L2.1, U9.11 (VIN); also elsewhere on the board
/acq_apd/APD_SHDN: R19.1, U9.12 (~SHDN); also elsewhere on the board
BIAS: C36.1, JP3.2, R21.1, U9.4 (VOUT); also elsewhere on the board
GND: C34.2, C35.2, C36.2, C37.2, P12.1, R19.2, R20.2, R23.2, R24.2, U9.7 (GND), U9.8 (SYNC), U9.10 (GND), U9.17 (GND); also elsewhere on the board
unnamed: C35.1, R24.1, U9.16 (MON)
unnamed: C37.1, R25.1
unnamed: L2.2, U9.5 (SW), U9.6 (SW)
unnamed: R20.1, U9.9 (RT)
unnamed: R21.2, R22.1, U9.3 (MONIN)
unnamed: R22.2, R23.1, U9.15 (FB)
unnamed: R25.2, U9.2 (APD)
unnamed: U9.13 (VREF), U9.14 (CTRL)

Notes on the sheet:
Acquisition bias supply
U9 bottom pad via

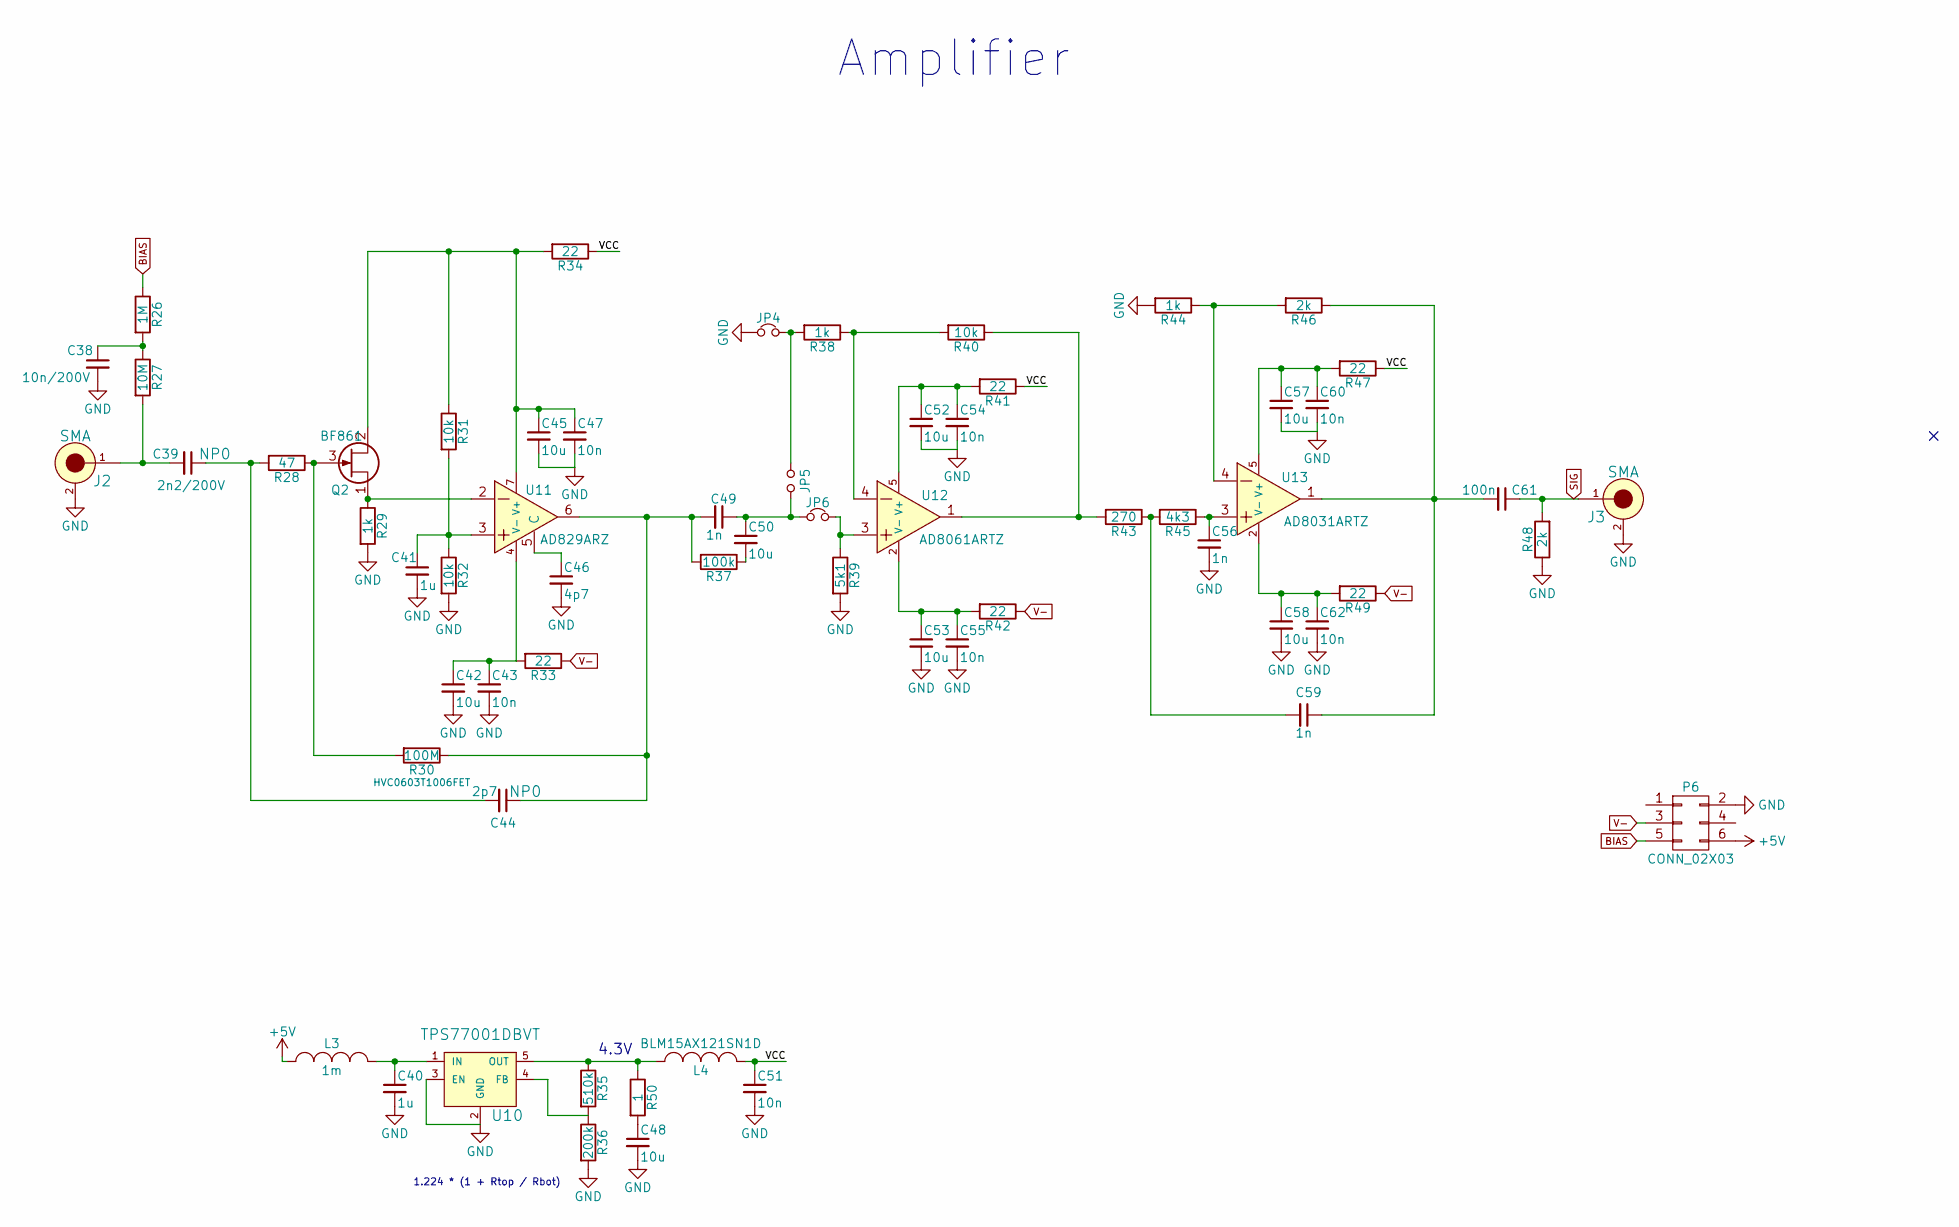
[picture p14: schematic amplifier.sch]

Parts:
C38: 10n/200V; R_0805
C39: 2n2/200V; R_0805
C40, C41: 1u; R_0402
C42, C45, C48, C50, C52, C53, C57, C58: 10u; R_0805
C43, C47, C51, C54, C55, C60, C62: 10n; R_0402
C44: 2p7; R_0402
C46: 4p7; R_0402
C49, C56, C59: 1n; R_0402
C61: 100n; R_0402
J2, J3: SMA; CON-SMA-EDGE
JP4, JP6: 0R; R_0402
JP5: DNP; R_0402
L3: 1m; SDR0302
L4: BLM15AX121SN1D; R_0402
P6: CONN_02X03; CONN_02x03_EDGE
Q2: BF861; SOT-23
R26: 1M; R_0402
R27: 10M; R_0402
R28: 47; R_0402
R29, R38, R44: 1k; R_0402
R30: 100M; R_0603
R31, R32, R40: 10k; R_0402
R33, R34, R41, R42, R47, R49: 22; R_0402
R35: 510k; R_0402
R36: 200k; R_0402
R37: 100k; R_0402
R39: 5k1; R_0402
R43: 270; R_0402
R45: 4k3; R_0402
R46, R48: 2k; R_0402
R50: 1; R_0402
U10: TPS77001DBVT; SOT-23-5
U11: AD829ARZ; SOIC-8_3.9x4.9mm_Pitch1.27mm
U12: AD8061ARTZ; SOT-23-5
U13: AD8031ARTZ; SOT-23-5

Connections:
+5V: L3.1, P6.6; also elsewhere on the board
/amplifier/VCC: C51.1, L4.2, R34.1, R41.1, R47.1
BIAS: P6.5, R26.1; also elsewhere on the board
GND: C38.2, C40.2, C41.2, C42.2, C43.2, C45.2, C46.2, C47.2, C48.2, C51.2, C52.2, C53.2, C54.2, C55.2, C56.2, C57.2, C58.2, C60.2, C62.2, J2.2, J2.3, J2.4, J2.5, J3.2, J3.3, J3.4, J3.5, JP4.1, P6.2, R29.2, R32.2, R36.2, R39.2, R44.2, R48.1, U10.2 (GND), U10.3 (EN); also elsewhere on the board
unnamed: C38.1, R26.2, R27.1
unnamed: C39.1, C44.2, R28.2
unnamed: C39.2, J2.1, R27.2
unnamed: C40.1, L3.2, U10.1 (IN)
unnamed: C41.1, R31.2, R32.1, U11.3
unnamed: C42.1, C43.1, R33.2, U11.4 (V-)
unnamed: C44.1, C49.2, R30.1, R37.2, U11.6
unnamed: C45.1, C47.1, Q2.2 (D), R31.1, R34.2, U11.7 (V+)
unnamed: C46.1, U11.5 (C)
unnamed: C48.1, R50.2
unnamed: C49.1, C50.1, JP5.2, JP6.1
unnamed: C50.2, R37.1
unnamed: C52.1, C54.1, R41.2, U12.5 (V+)
unnamed: C53.1, C55.1, R42.2, U12.2 (V-)
unnamed: C56.1, R45.1, U13.3
unnamed: C57.1, C60.1, R47.2, U13.5 (V+)
unnamed: C58.1, C62.1, R49.2, U13.2 (V-)
unnamed: C59.1, C61.2, R46.1, U13.1
unnamed: C59.2, R43.1, R45.2
unnamed: JP4.2, JP5.1, R38.2
unnamed: JP6.2, R39.1, U12.3
unnamed: L4.1, R35.1, R50.1, U10.5 (OUT)
unnamed: Q2.1 (S), R29.1, U11.2
unnamed: Q2.3 (G), R28.1, R30.2
unnamed: R35.2, R36.1, U10.4 (FB)
unnamed: R38.1, R40.2, U12.4
unnamed: R40.1, R43.2, U12.1
unnamed: R44.1, R46.2, U13.4
SIG: C61.1, J3.1, R48.2; also elsewhere on the board
V-: P6.3, R33.1, R42.1, R49.1; also elsewhere on the board

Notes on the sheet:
Amplifier
4.3V
1.224 * (1 + Rtop / Rbot)

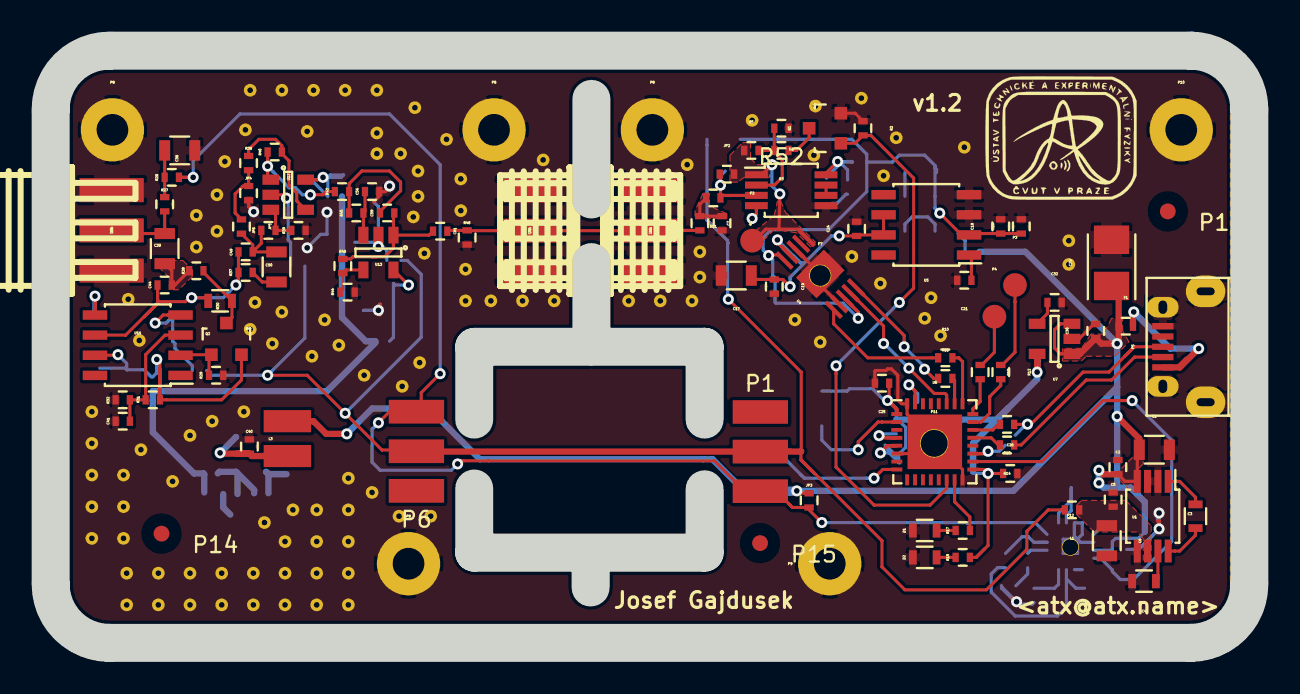
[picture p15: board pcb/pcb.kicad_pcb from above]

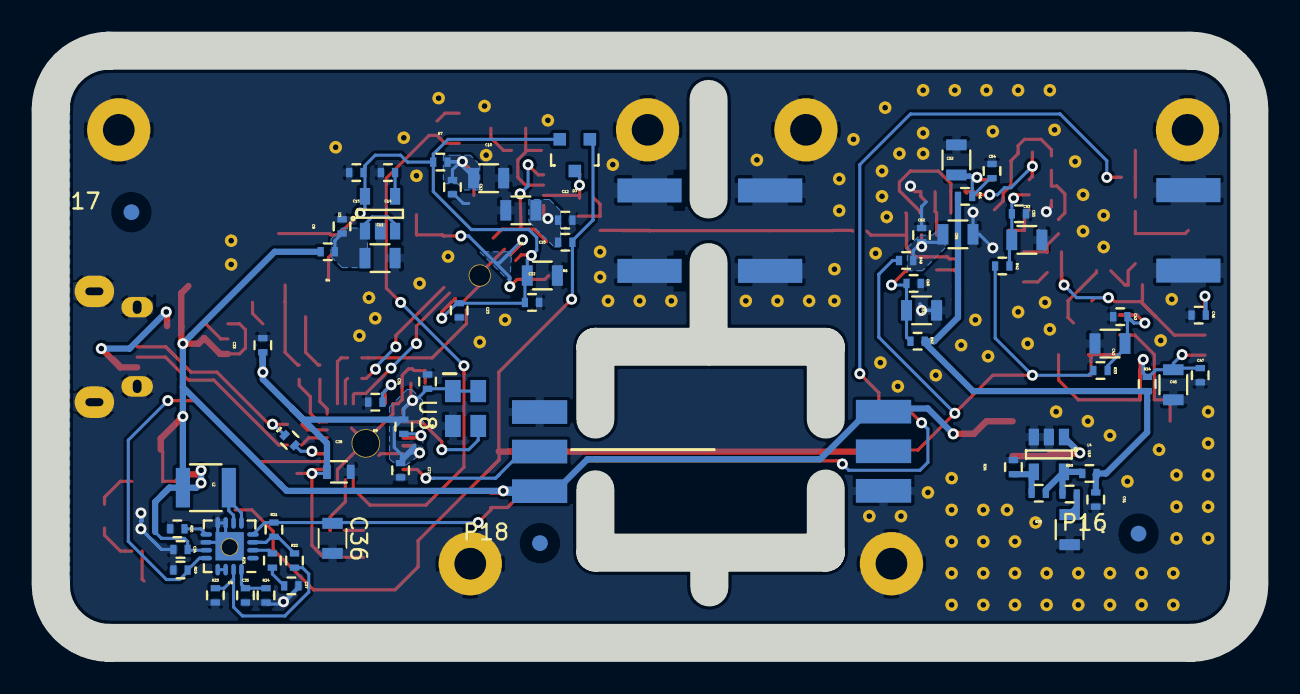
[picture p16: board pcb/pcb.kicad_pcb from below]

Board: 2 copper layers, 75.7 x 37.4 mm, 166 parts (66 on the bottom side), 85 nets.

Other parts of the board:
P8#2, P8#3, P8#4: TST; Measurement_Point_Round-TH_Big

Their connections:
GND: P8#2.1, P8#3.1, P8#4.1; also elsewhere on the board

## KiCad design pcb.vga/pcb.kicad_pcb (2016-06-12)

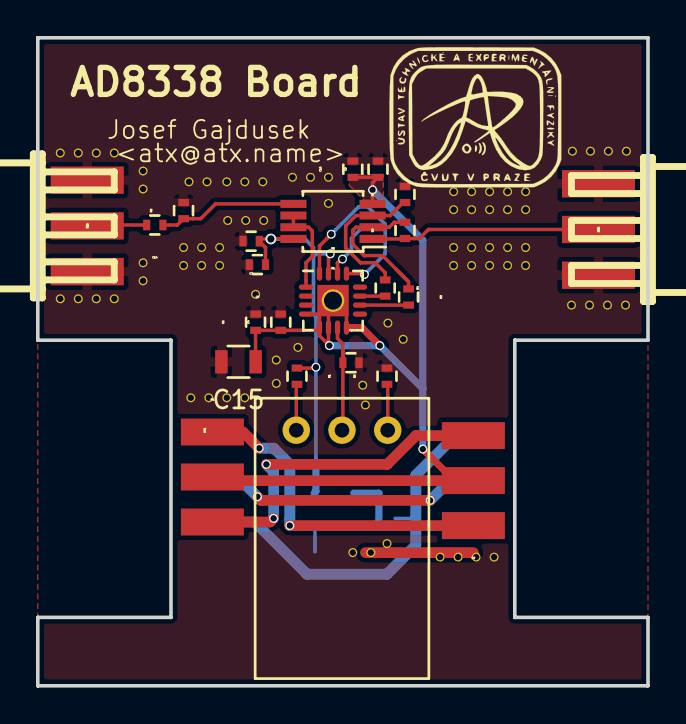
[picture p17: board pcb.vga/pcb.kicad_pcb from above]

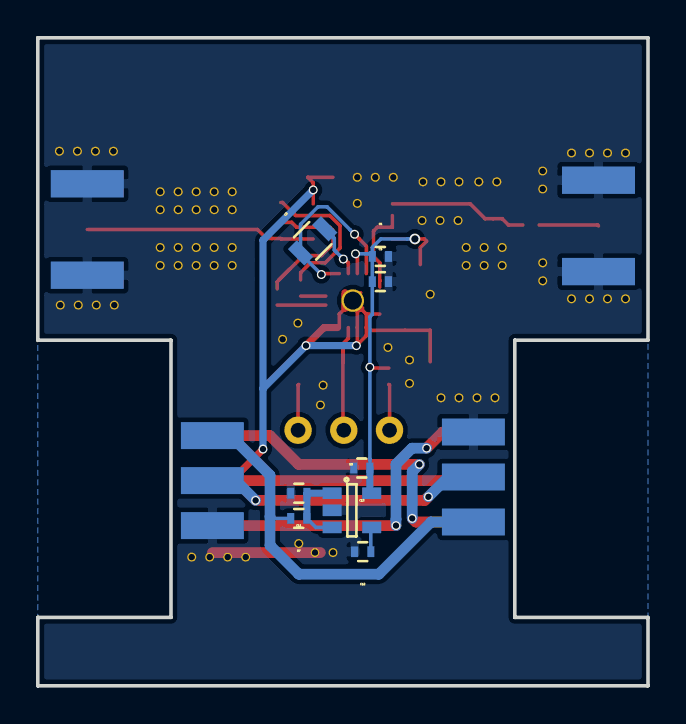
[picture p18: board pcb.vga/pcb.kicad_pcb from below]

Board: 2 copper layers, 33.9 x 36.0 mm, 31 parts (8 on the bottom side), 22 nets.

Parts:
C1, C3, C4, C7, C8: 10n; R_0402
C2, C15: 10u; R_0805
C5, C6, C9, C10, C12: 100n; R_0402
C11, C13: 1u; R_0402
C14: DNP; R_0402
J1, J2: SMA; CON-SMA-EDGE
P1: CONN_IN; CONN_02x03_EDGE
P2: CONN_OUT; CONN_02x03_EDGE
R1: 43k; R_0402
R2: 18k; R_0402
R3, R4, R5, R6: 10k; R_0402
R7: 22; R_0402
R8: 1M; R_0402
RV1: 20k; Potentiometer_Bourns_3296W_3-8Zoll_Inline_ScrewUp_Side
U1: MAX4477; MSOP-8_3x3mm_Pitch0.65mm
U2: AD8338; UQFN-16-1EP_3x3mm_Pitch0.5mm
U3: NCP700B; SOT-23-5

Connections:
+3V3: C3.1, C5.1, C7.1, C9.1, C13.1, R1.1, U1.8, U2.15, U3.5
+5V: P1.6, P2.6, R7.2
GND: C1.2, C3.2, C4.2, C5.2, C6.2, C7.2, C8.2, C9.2, C10.2, C11.2, C12.2, C13.2, C15.2, J1.2, J1.3, J1.4, J1.5, J2.2, J2.3, J2.4, J2.5, P1.2, P2.2, R2.2, R5.2, R8.2, U3.2
unnamed: C1.1, RV1.2, U2.7
unnamed: C2.1, U2.13, U2.16
unnamed: C2.2, U2.14
unnamed: C11.1, R7.1, U3.1, U3.3
unnamed: C12.1, U3.4
unnamed: C14.1, R8.1, U1.5
unnamed: C14.2, J1.1
unnamed: J2.1, R6.1, U1.1
unnamed: P1.1, P2.1
unnamed: P1.4, P2.4
unnamed: P1.5, P2.5
unnamed: R1.2, RV1.3
unnamed: R2.1, RV1.1
unnamed: R3.1, R6.2, U1.2
unnamed: R3.2, U2.10
unnamed: R4.1, R5.1, U1.3
unnamed: R4.2, U2.11
unnamed: U1.6, U1.7, U2.1
V-: C4.1, C6.1, C8.1, C10.1, C15.1, P1.3, P2.3, U1.4, U2.4, U2.5, U2.6, U2.8, U2.17

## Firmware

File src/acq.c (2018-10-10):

/* 
 * Copyright (C) 2016 Institute of Applied and Experimental Physics (http://www.utef.cvut.cz/)
 *
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
 * You should have received a copy of the GNU Lesser General Public License
 * along with this program.  If not, see <http://www.gnu.org/licenses/>.*
 */

#include <strings.h>
#include <libopencm3/cm3/nvic.h>
#include <libopencm3/stm32/gpio.h>
#include <libopencm3/stm32/dma.h>
#include <libopencm3/stm32/rcc.h>
#include <libopencm3/stm32/spi.h>

#include "acq.h"
#include "prios.h"
#include "utils.h"

#define SPI_C1		SPI3
#define BANK_CS		GPIOA
#define GPIO_CS		GPIO15
#define BANK_SCLK	GPIOB
#define GPIO_SCLK	GPIO3
#define BANK_DOUT	GPIOB
#define GPIO_DOUT	GPIO4

#define BANK_AMP	GPIOA
#define GPIO_AMP	GPIO7

struct acq_state acq_channel = {
	.threshold = 100,
	.rthresh = 0,
};

#pragma GCC push_options
#pragma GCC optimize ("O3")

#define BANK_LED		GPIOB
#define GPIO_LED		GPIO0

inline static void led_on()
{
	gpio_set(BANK_LED, GPIO_LED);
}

inline static void led_toggle()
{
	gpio_toggle(BANK_LED, GPIO_LED);
}

RAMFUNC
void dma1_channel2_isr(void)
{
	int off = DMA1_ISR & DMA_ISR_HTIF2 ? 0 : BUFFER_SIZE / 2 ;
	uint16_t data;

	DMA1_IFCR = DMA_IFCR_CHTIF2 | DMA_IFCR_CTCIF2;

	for (int i = 0; i < BUFFER_SIZE / 2; i++) {
		data = acq_channel.buff[off + i];
		if (acq_channel.pulse) {
			if (data < acq_channel.threshold) {
				acq_channel.pulse = false;
				if (acq_channel.rthresh == 0 ||
						(acq_channel.rthresh != 0 && acq_channel.falling > acq_channel.rthresh)) {
					comm_send_event(acq_channel.max);
				}
			} else {
				if (data > acq_channel.max) {
					acq_channel.falling--;
					acq_channel.max = data;
				} else {
					acq_channel.falling++;
				}
			}
		} else {
			if (data > acq_channel.threshold) {
				acq_channel.max = data;
				acq_channel.falling = -1;
				acq_channel.pulse = true;
			}
		}
	}
}

#pragma GCC pop_options

static void acq_spi_init(uint32_t spi)
{
	spi_reset(spi);
	spi_init_master(spi,
					SPI_CR1_BAUDRATE_FPCLK_DIV_2,
					SPI_CR1_CPOL_CLK_TO_0_WHEN_IDLE,
					SPI_CR1_CPHA_CLK_TRANSITION_1,
					0,
					SPI_CR1_MSBFIRST);

	spi_set_data_size(spi, SPI_CR2_DS_14BIT);
	spi_set_receive_only_mode(spi);
	spi_fifo_reception_threshold_16bit(spi);
	SPI_CR2(spi) |= SPI_CR2_NSSP;
	spi_enable_rx_buffer_not_empty_interrupt(spi);
}

void acq_init()
{
	/* Initialize amplifier control GPIO */
	gpio_mode_setup(BANK_AMP, GPIO_MODE_OUTPUT, GPIO_PUPD_NONE, GPIO_AMP);
	gpio_clear(BANK_AMP, GPIO_AMP);
	gpio_mode_setup(BANK_LED, GPIO_MODE_OUTPUT, GPIO_PUPD_NONE, GPIO_LED);
	gpio_clear(BANK_LED, GPIO_LED);

	/* Initialize SPI GPIOs */
	gpio_mode_setup(BANK_CS, GPIO_MODE_AF, GPIO_PUPD_NONE, GPIO_CS);
	gpio_mode_setup(BANK_SCLK, GPIO_MODE_AF, GPIO_PUPD_NONE, GPIO_SCLK);
	gpio_mode_setup(BANK_DOUT, GPIO_MODE_AF, GPIO_PUPD_NONE, GPIO_DOUT);

	gpio_set_af(BANK_CS, GPIO_AF6, GPIO_CS);
	gpio_set_af(BANK_SCLK, GPIO_AF6, GPIO_SCLK);
	gpio_set_af(BANK_DOUT, GPIO_AF6, GPIO_DOUT);

	rcc_periph_clock_enable(RCC_SPI3);

	acq_spi_init(SPI_C1);

	rcc_periph_clock_enable(RCC_DMA1);
	dma_channel_reset(DMA1, DMA_CHANNEL2);
	dma_disable_channel(DMA1, DMA_CHANNEL2);

	dma_set_peripheral_address(DMA1, DMA_CHANNEL2, (uint32_t)&SPI_DR(SPI_C1));
	dma_set_memory_address(DMA1, DMA_CHANNEL2, (uint32_t)&acq_channel.buff);
	dma_set_number_of_data(DMA1, DMA_CHANNEL2, BUFFER_SIZE);

	dma_set_priority(DMA1, DMA_CHANNEL2, DMA_CCR_PL_MEDIUM);

	dma_set_memory_size(DMA1, DMA_CHANNEL2, DMA_CCR_MSIZE_16BIT);
	dma_set_peripheral_size(DMA1, DMA_CHANNEL2, DMA_CCR_PSIZE_16BIT);
	dma_enable_memory_increment_mode(DMA1, DMA_CHANNEL2);
	dma_set_read_from_peripheral(DMA1, DMA_CHANNEL2);
	dma_enable_circular_mode(DMA1, DMA_CHANNEL2);

	nvic_set_priority(NVIC_DMA1_CHANNEL2_IRQ, PRIO_ACQ);
}

static bool acq_amp_enabled = false;

bool acq_amp_isenabled()
{
	return acq_amp_enabled;
}

void acq_amp_enable()
{
	acq_amp_enabled = true;
	gpio_set(BANK_AMP, GPIO_AMP);
}

void acq_amp_disable()
{
	acq_amp_enabled = false;
	gpio_clear(BANK_AMP, GPIO_AMP);
}

void acq_start()
{
	spi_enable(SPI_C1);

	spi_enable_rx_dma(SPI_C1);
	dma_enable_transfer_complete_interrupt(DMA1, DMA_CHANNEL2);
	dma_enable_half_transfer_interrupt(DMA1, DMA_CHANNEL2);
	dma_enable_channel(DMA1, DMA_CHANNEL2);
	nvic_enable_irq(NVIC_DMA1_CHANNEL2_IRQ);
}

void acq_pause()
{
	gpio_clear(BANK_LED, GPIO_LED);
	spi_disable(SPI_C1);
	spi_disable_rx_dma(SPI_C1);
	dma_disable_transfer_complete_interrupt(DMA1, DMA_CHANNEL2);
	dma_disable_half_transfer_interrupt(DMA1, DMA_CHANNEL2);
	dma_disable_channel(DMA1, DMA_CHANNEL2);
	nvic_disable_irq(NVIC_DMA1_CHANNEL2_IRQ);
}

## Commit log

2016-05-31 Initial commit #2
    [acq_adc.sch, acq_apd.sch, acq_mcu.sch, amplifier.sch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]
2016-06-12 pcb: Update to v1.1
    Changes:
    Add input protection diodes to acquisition board
    Add second screw hole to the preamplifier
    Add PCB revision number to the board
    LPF->HPF at the output of the preamplifier board
    Fix connector orientation on the preamplifier board
    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
    [acq_adc.sch, acq_apd.sch, acq_mcu.sch, amplifier.sch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]
2016-06-12 pcb.vga: Add the AD8338 board
    Also accidentaly added some changes which belonged to 2e3d88cac247fd0d2ffe4990b1f29d498317d67b
    but too lazy to fix
    [pcb-B.Cu.gbl, pcb-B.Mask.gbs, pcb-B.SilkS.gbo, pcb-F.Cu.gtl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]
2016-06-23 pcb: Add .pdf and remove plot files
    [bot.gbr, mill.gbr, pcb-B.Cu.gbl, pcb-B.Mask.gbs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]
2016-07-25 ieapspect-filedump: Update so that it actually works with the current library
2017-08-15 pcb: Update to the current iteration
    Looks like I forgot to commit the changes made for manufacturing...
    [acq_adc.sch, acq_apd.sch, acq_mcu.sch, amplifier.sch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]
2017-08-21 src|bootloader: Uncomment info printfs in Makefiles
2017-12-15 pcb.diode: Add
    [panel.kicad_pcb, pcb.kicad_pcb, pcb.sch]
2018-05-18 mechanical: diode: Add
    [diode.scad]

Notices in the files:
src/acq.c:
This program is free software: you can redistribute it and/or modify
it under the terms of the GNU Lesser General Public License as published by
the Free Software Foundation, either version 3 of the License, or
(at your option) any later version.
